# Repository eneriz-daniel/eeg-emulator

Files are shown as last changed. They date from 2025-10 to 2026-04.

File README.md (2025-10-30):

# EEG Emulation and Acquisition

> Documentation is available at: [https://eneriz-daniel.com/eeg-emulator/](https://eneriz-daniel.com/eeg-emulator/)

This repository contains the design files, code, and documentation for an EEG
emulation and acquisition system. The system is designed to emulate an EEG headset
using a custom PCB that demultiplexes signals from a National Instruments
USB-6212 Data Acquisition (DAQ) device, and to acquire EEG signals using an ADS1299
Analog-to-Digital Converter (ADC) connected to an Arduino Nano 33 BLE Sense.

## Repository Structure

The repository is organized into the following main directories and files:

- `docs/`: Documentation files for the project
    - `ads1299_driver/`: Python API reference for the ADS1299 driver
    - `assets/`: Images and diagrams used in documentation
    - `datasheets/`: Component datasheets and manuals
  
- `eeg_acquisition/`: EEG signal acquisition system components
    - `ADS1299driver.py`: Python wrapper for the ADS1299 driver
    - `design_files/`: KiCAD PCB and schematic files for the acquisition board
    - `micro/`: Arduino firmware for the ADS1299 driver
        - `src/`: C++ source code for the driver implementation

- `eeg_emulation/`: EEG signal emulation system components
    - `daq.py`: Python script for controlling the NI USB-6212 DAQ
    - `design_files/`: KiCAD PCB and schematic files for the demultiplexer board

- `test.py`: Example script demonstrating the integration between the EEG emulation and acquisition systems, including configuration of the ADS1299, signal generation, data acquisition, and visualization

## Requirements

### Software

- [Python](https://www.python.org/) 3.13 or later (for running the code and documentation)
    - Package manager, [`uv`](https://docs.astral.sh/uv/)
- [KiCAD](https://www.kicad.org/) 9 or later (for PCB design files)
- [PlatformIO](https://platformio.org/) (for Arduino development)

### Commercial hardware

- National Instruments NI USB-6212 Data Acquisition device

## Installation

- Clone the repository:

    ```bash
    git clone https://github.com/eneriz-daniel/eeg-emulator.git
    ```

- Install the required packages:

    ```bash
    uv sync --all-groups
    ```

## Software commands

- To serve the documentation locally:

    ```bash
    uv run mkdocs serve
    ```

- To check linting and formatting:

    ```bash
    uv run ruff check
    ```

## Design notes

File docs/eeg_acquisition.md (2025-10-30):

## The ADC

We have selected the [ADS1299](datasheets/ads1299.pdf) as the Anaglog-to-Digital
Converter (ADC) for our EEG acquisition system. The ADS1299 is a low-power,
24-bit, 8-channel ADC designed specifically for biopotential measurements,
making it an ideal choice for EEG applications. It features a high input impedance,
low noise, and a built-in programmable gain amplifier (PGA), which allows for
accurate signal acquisition from the scalp electrodes.

The ADS1299 can be connected to a microcontroller using the SPI interface,
which allows for fast data transfer and control of the ADC settings. We have created
an schematic design on a Kicad project to document how we have connected the
ADS1299 to an Arduino Nano 33 BLE Sense. The schematic includes the necessary
connections for power supply, ground, and the SPI interface. These schematic files
are available at `eeg_acquisition/design_files`.

## The driver

We have extended an existing driver for the ADS1299 to provide an interface through
serial communication. The driver is written in C++ and it includes functions for
initializing the ADC, configuring the settings, and reading the data from the ADC.
This driver has been tested with the Arduino Nano 33 BLE Sense and it is compatible with
the Arduino IDE and PlatformIO. The driver is available at `eeg_acquisition/micro`, and it is
composed of two main files:

- `ADS1299.cpp` contains the low-level implementation of the driver, including the
SPI commands to configure the ADC and read the data. The driver uses the Arduino SPI library
to communicate with the ADS1299.

- `ADS1299Manager.cpp` contains the high-level implementation of the driver, including
the functions to initialize the ADC, configure the settings, and read the data.
It also provides the functionality to interface with serial communication, allowing
for easy integration with other systems.

Additionally, we have created a Python wrapper for the driver, available at
`eeg_acquisition/ADS1299driver.py`. This wrapper is able to communicate with the
Arduino board through serial communication, allowing for easy integration with
Python applications. The wrapper includes functions for configuring the ADC,
reading the data and even live plotting the acquired signals, as shown below.
A complete reference for the wrapper is available [here](ads1299_driver/python.md).

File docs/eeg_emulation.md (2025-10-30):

EEG Demultiplexer PCB

## Introduction

We have designed a PCB to emulate an EEG headset by demultiplexing the
signals from a multiplexed EEG signal provided by a Data Acquisition (DAQ) device,
a [National Instruments USB-6212](datasheets/usb-621x-manual.pdf).

## Description of the PCB

The design files and schematics of the PCB are available in the `eeg_demultiplexer/design_files`
directory.

### Analog part

The PCB is designed to demultiplex the 8 channels of the EEG signal from the DAQ
device, thus it has an analog input `EEG` and 8 main outputs `AOUT0` to `AOUT7`.

The analog input `EEG` must be in the range of 0-5V, since it is demultiplexed
with a [74HC4051](datasheets/74HC_HCT4051.pdf) analog demultiplexer. The outputs
of the demultiplexer are connected to the connections `A0` to `A7`,
which can be useful for debugging purposes.

Then, the signal is passed through the following sample-and-hold circuit, which is
followed by a voltage divider.

EEG Demultiplexer Analog Part

The sample-and-hold circuit is built with diode, a 1nF capacitor and a
[TL082](datasheets/tl082.pdf) operational amplifier. The diode and the capacitor
are used to sample the signal coming from the demultiplexer. A switch is used to
to short the capacitor to ground to discharge it before sampling the next
signal. The switch is controlled by the `DCHG` signal.

The operational amplifier is configured with a non-inverting gain of 2 by using
resistors with the same value of 2.1kΩ. Additionally, setting the
reference of the feedback at +5V allows to offset the output voltage by -5V.

The output of the operational amplifier is externalized to the `AAMP0` to `AAMP7`
connections, which can be useful for debugging purposes.

Finally, the output of the operational amplifier is passed through a voltage divider
to reduce the voltage in a factor of 5000, using a resistors of 2MΩ and 400Ω.

### Digital part

To control the selected channel of the demultiplexer, the PCB has a [74HC191](datasheets/74HC191.pdf)
counter. The counter is configured to count up. It has 4 parallel inputs which are loaded
when the `CP` signal is low. The default value to be loaded in the counter is 7.
This counter is clocked with the `CLK` signal. The three least significant
outputs of the counter are used as the channel selection signals, they are connected
to the demultiplexer channel selection, and can be consulted at the `CHAN0` to `CHAN2`
connections.

Two 2-input AND gates are used to know when the counter has reached the value 7. This
gates are available in the [74HC08D](datasheets/74HC_HCT08.pdf) package.
The output of the AND gates is connected to one of the pins of jumper `J13`. Other
pin of the jumper `J13` is connected to the total count signal of the counter, which
is 1 when the counter has reached the value 15. The default position of the jumper
`J13` is to connect its central pin to the output of the AND gates, which identifies when the
counter has reached the value 7.

The central pin of the jumper `J13` is connected to the control of two switches [ADG719](datasheets/ADG719.pdf).
The input of the first switch is connected to the `CLK` signal, and the output
is connected to the `START` signal, which can be used to trigger the conversion
of an ADC sampling the demultiplexed signals. The input of the second switch is
connected to the negated `CLK` signal, which is generated with an inverter [74HC04](datasheets/74HC_HCT1G04.pdf).
The output of this second switch is connected to the `DISCHARGE` signal, which
is used to discharge the capacitor of the sample-and-hold circuit.

Therefore, the following diagram shows the behavior of the digital part of the PCB:

```kroki-wavedrom
{ signal:
    [
      { name: 'CLK',      wave: 'P........', period: 2},
      { name: 'CHAN',     wave: '=========', data: ['0', '1', '2', '3', '4', '5', '6', '7', '0'], period: 2},
      { name: 'J16',      wave: '0......10', period: 2},
      { name: 'START',    wave: '0.............10..'},
      { name: '~CLK',     wave: 'N........', period: 2},
      { name: 'DISCARGE', wave: '0..............10.'},
    ]
}
```

## PCB characterization

To ensure the PCB is working properly, we have coded a simple test program,
`eeg_emulation/daq.py`, that uses the [nidaqmx](https://pypi.org/project/nidaqmx/)
library to control a National Instruments USB-6212 DAQ device. This program configures
the DAQ to:

- Ensure the channel in the counter of the PCB is set to 7.
- Create a clock signal `CTR0`, whose output is at `PFI12` pin of the DAQ.
- Create an analog output signal with the multiplexed EEG signal at pin `AO0`
  using the signal at `PFI0` as clock signal.
- Set 8 analog input pins to read the demultiplexed signals before the voltage
  divider. The pins of the PCB are `AAMP0` to `AAMP7`, and the pins of the DAQ
  are `AI0` to `AI7`. This conversion is triggered by the `START` signal, which
  is connected to the  `PFI2` pin of the DAQ device.

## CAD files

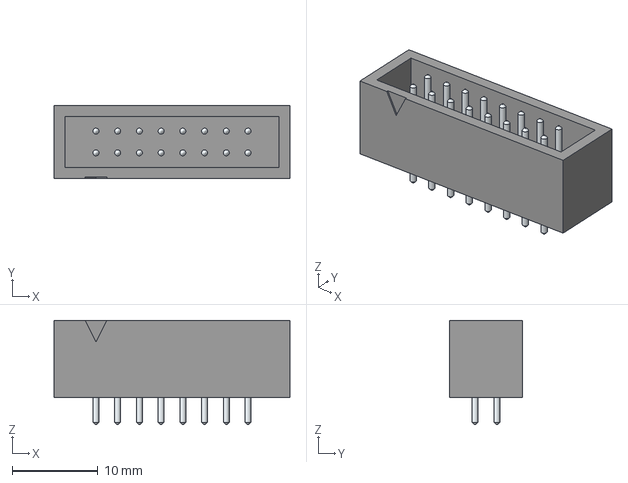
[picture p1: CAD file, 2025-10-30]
eeg_acquisition/design_files/3d-files/XG4C-1631.step
27.6 x 8.50 x 12.2 mm
LeadsArray

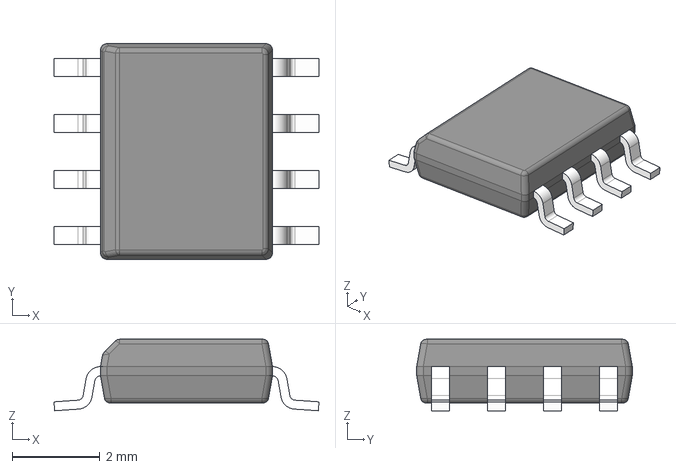
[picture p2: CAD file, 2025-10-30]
eeg_emulation/design_files/3d-models/LM2663MX_NOPB.stp
6.02 x 4.90 x 1.63 mm
BODY-SO
LEAD-D0008A x 8

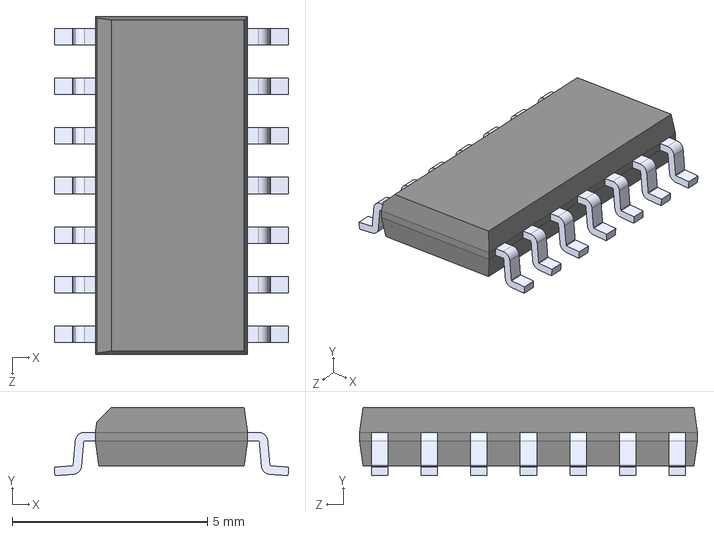
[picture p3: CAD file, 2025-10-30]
eeg_emulation/design_files/3d-models/74HC08D_653.step
6.00 x 1.75 x 8.65 mm

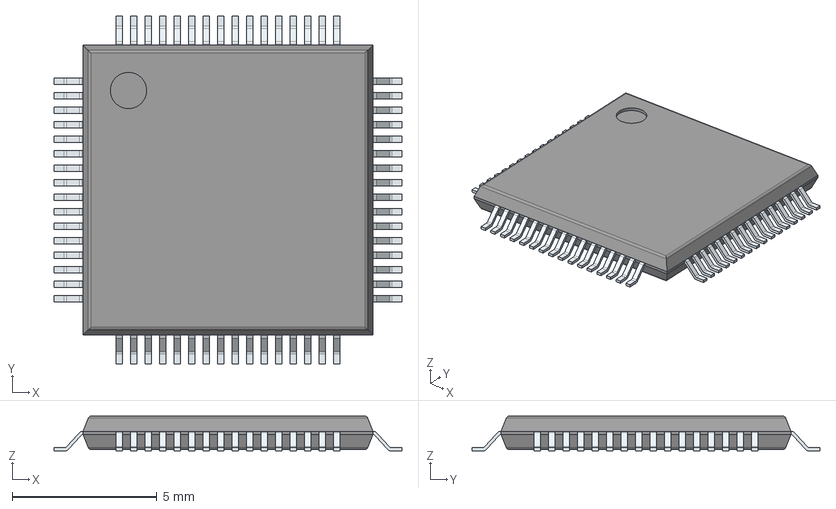
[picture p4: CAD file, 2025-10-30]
eeg_acquisition/design_files/3d-files/ADS1299-6PAG.step
12.0 x 12.0 x 1.20 mm
PinsArrayLR
PinsArrayTB

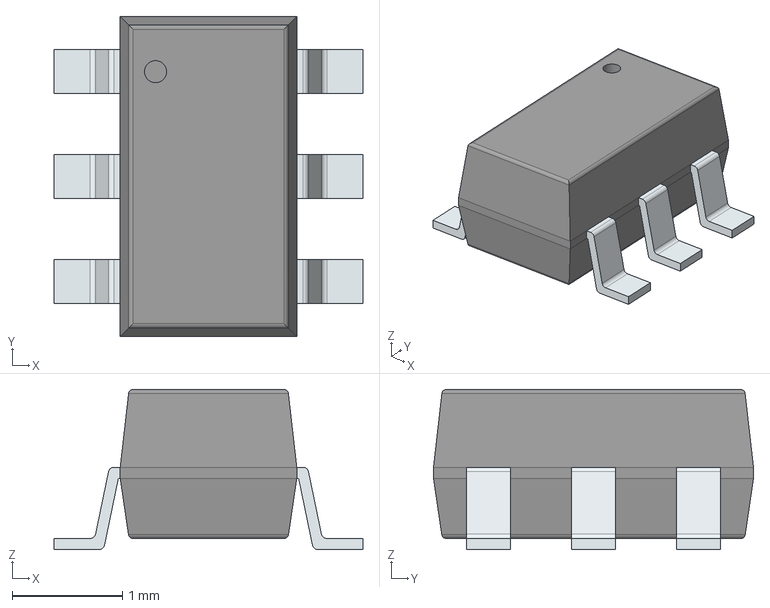
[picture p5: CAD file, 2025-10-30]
eeg_emulation/design_files/3d-models/ADG719BRTZ-REEL.step
2.80 x 2.90 x 1.45 mm
PinsArrayLR

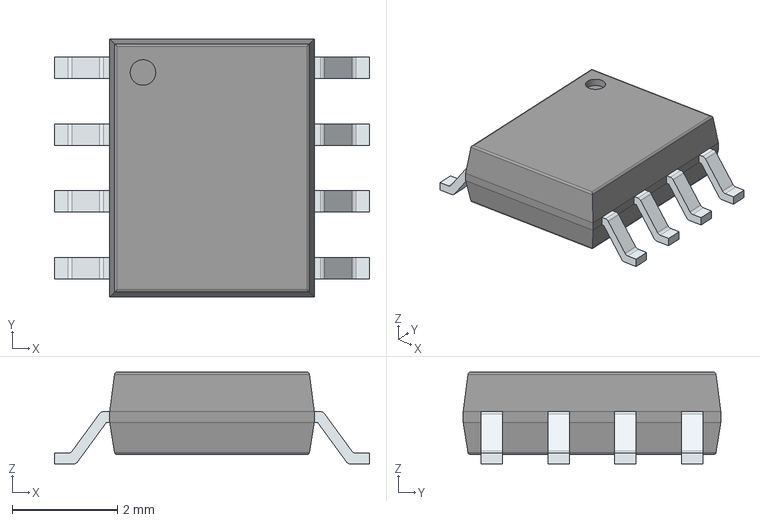
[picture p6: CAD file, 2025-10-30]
eeg_emulation/design_files/3d-models/TL082ID.step
6.00 x 4.91 x 1.75 mm
PinsArrayLR

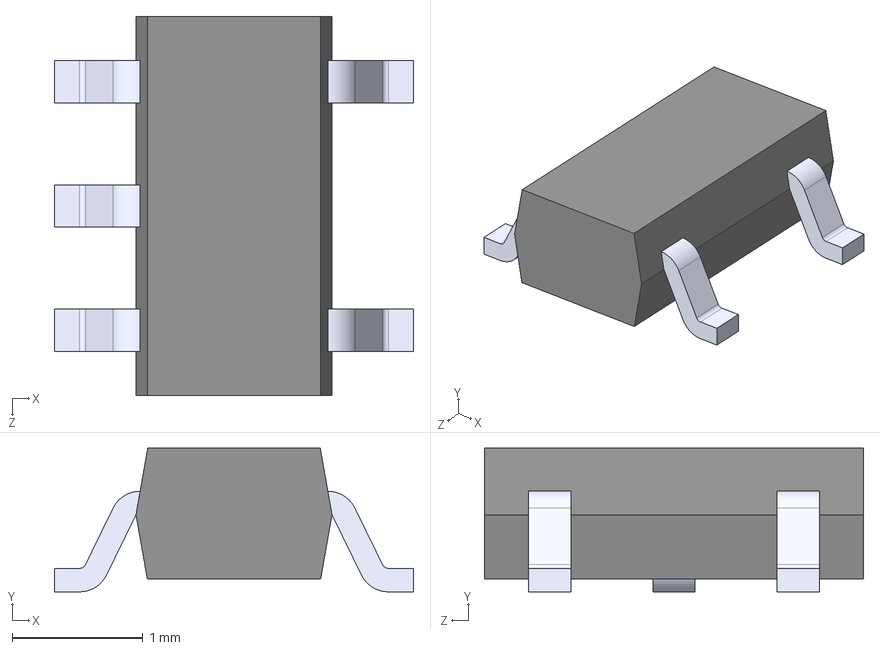
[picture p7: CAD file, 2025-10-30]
eeg_emulation/design_files/3d-models/74HC1G04GV,125.STEP
2.75 x 1.10 x 2.90 mm

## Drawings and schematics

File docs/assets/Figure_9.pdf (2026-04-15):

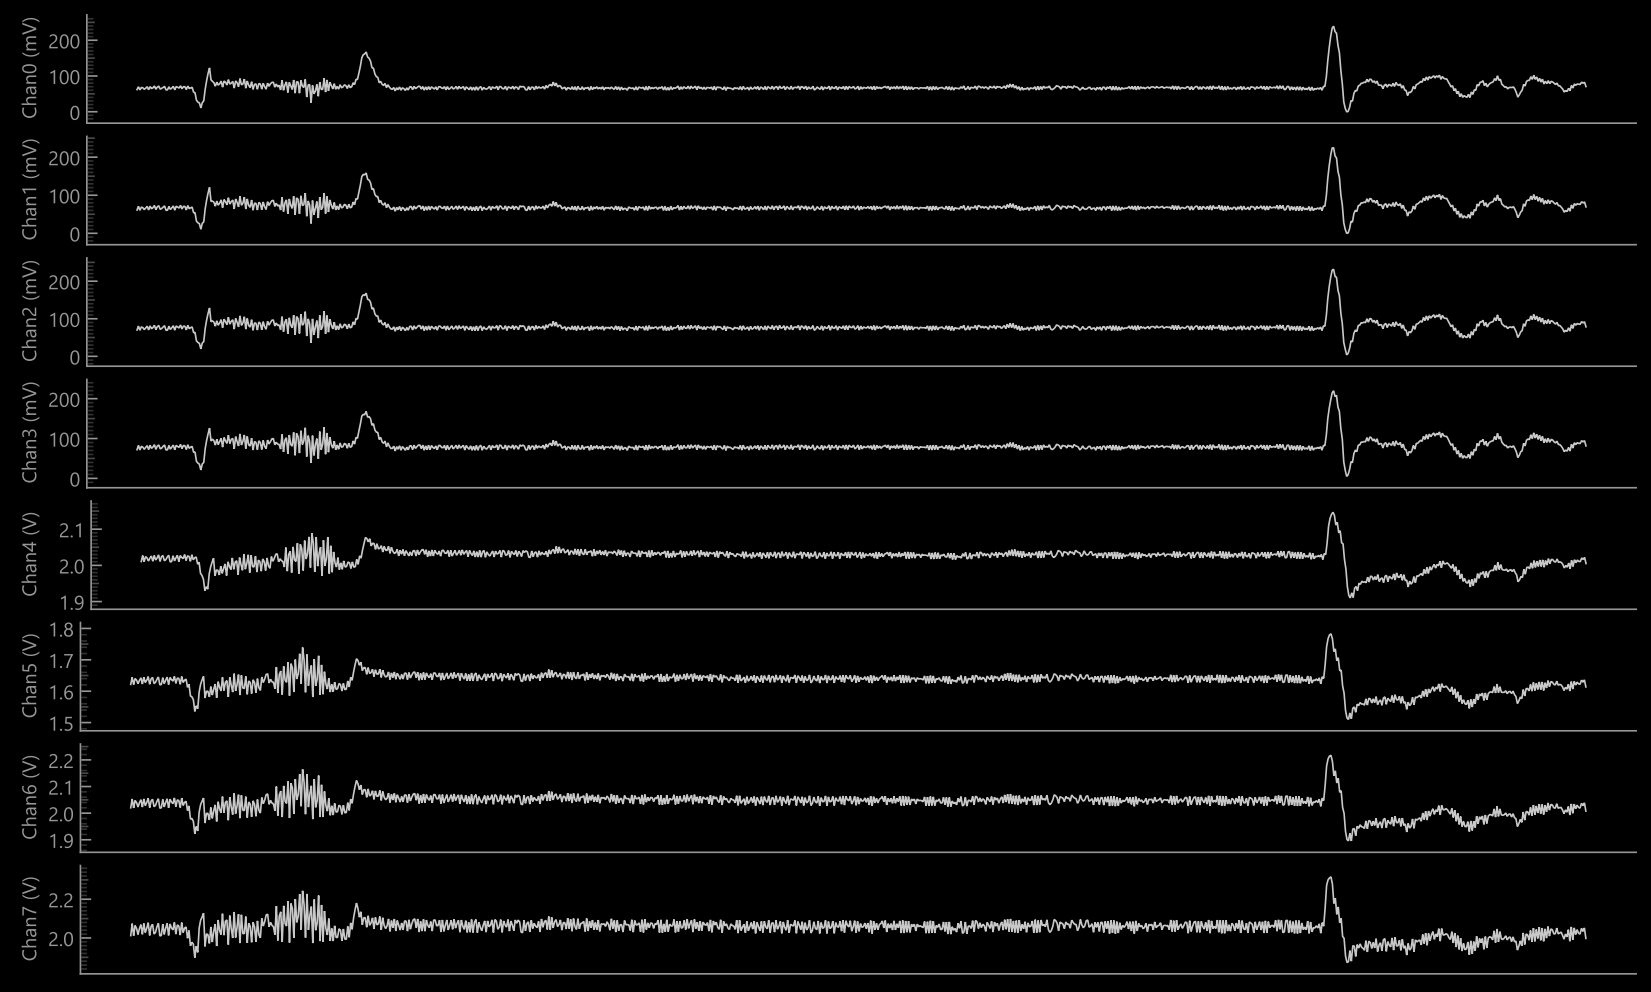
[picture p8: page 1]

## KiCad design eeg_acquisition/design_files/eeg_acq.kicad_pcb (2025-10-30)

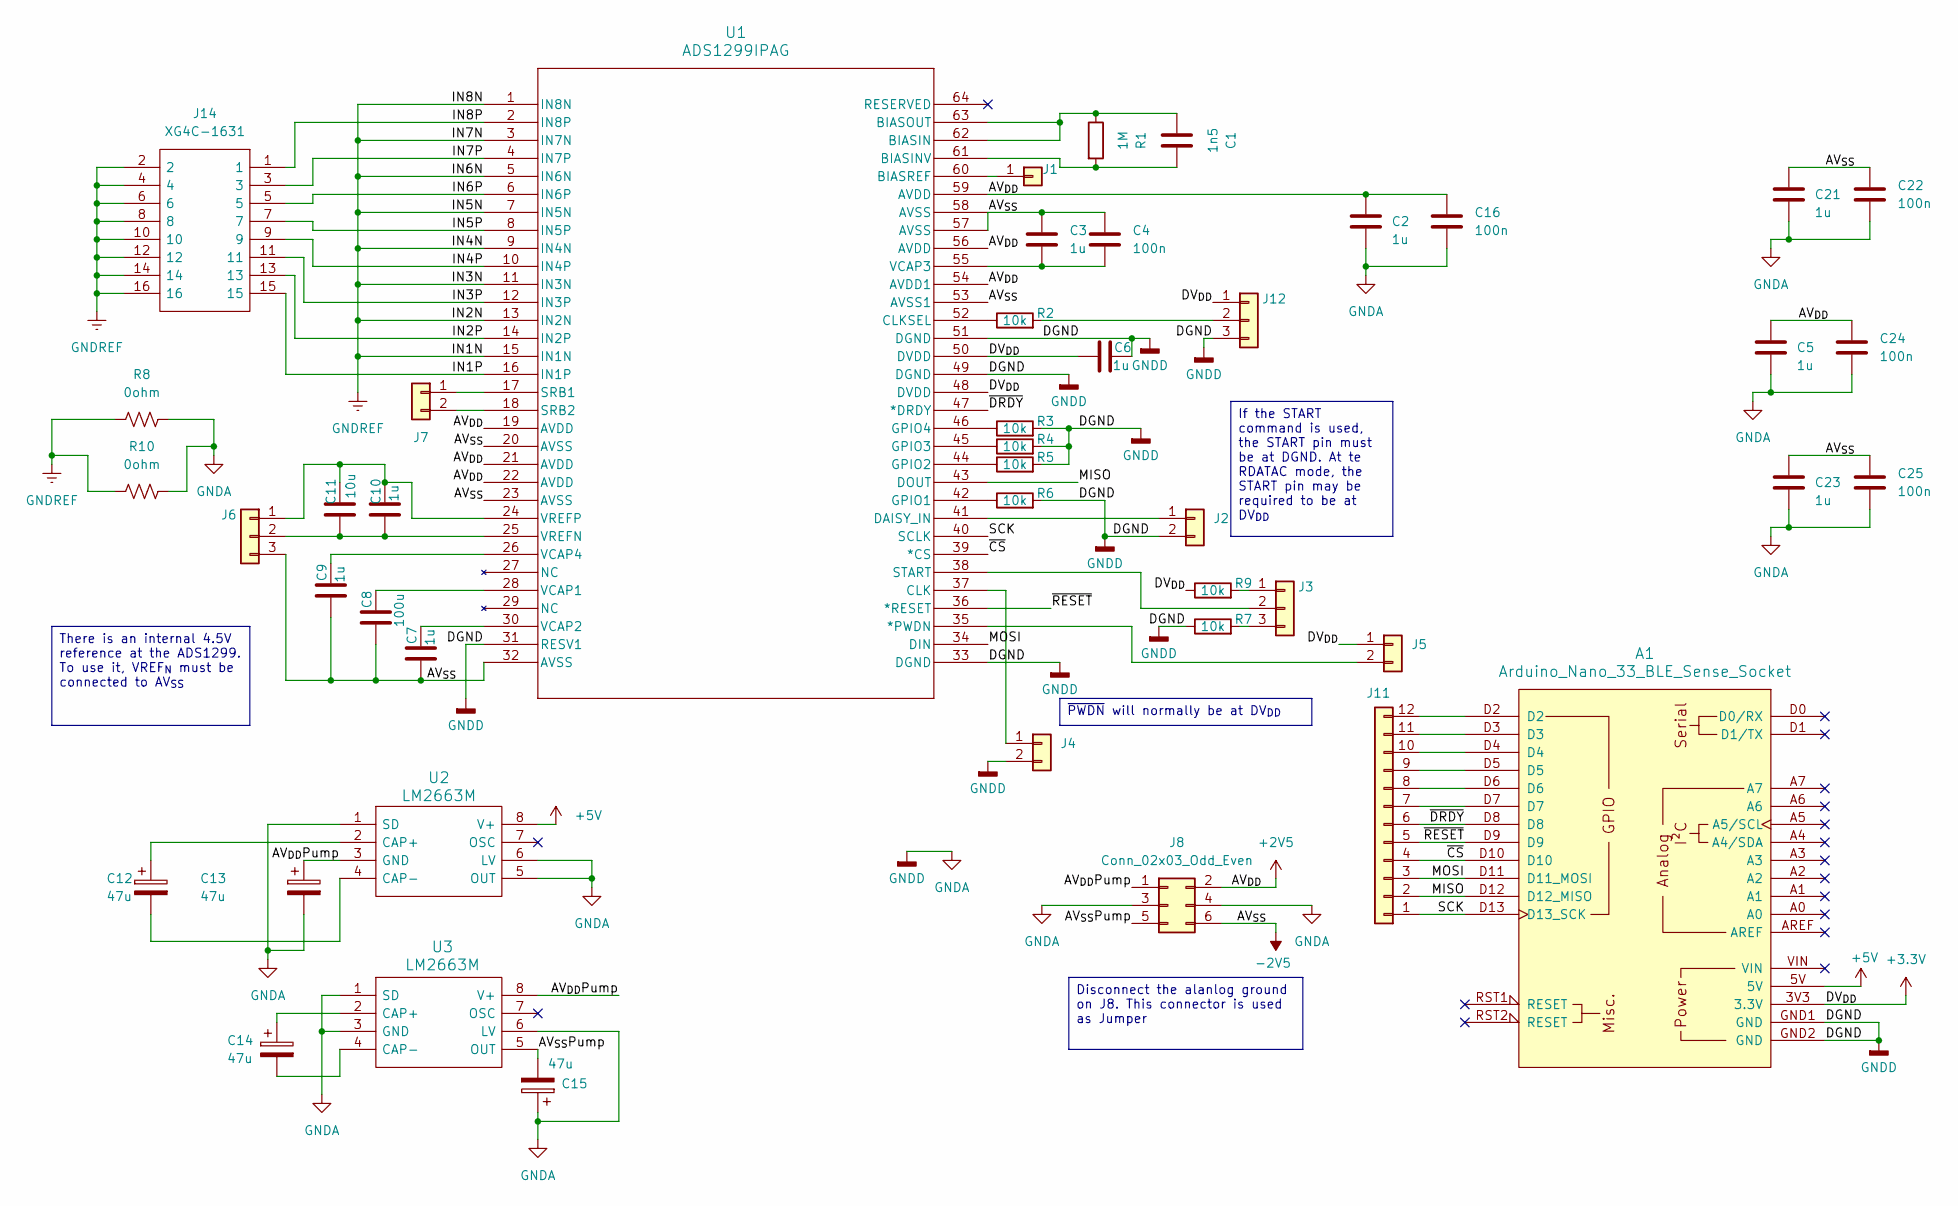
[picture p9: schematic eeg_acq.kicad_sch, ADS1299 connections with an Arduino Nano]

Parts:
A1: Arduino_Nano_33_BLE_Sense_Socket; Arduino_Nano_Every_Socket
C1: 1n5; C_0603_1608Metric_Pad1.08x0.95mm_HandSolder
C2, C3, C5, C6, C7, C9, C10, C21, C23: 1u; C_0603_1608Metric_Pad1.08x0.95mm_HandSolder
C4, C16, C22, C24, C25: 100n; C_0603_1608Metric_Pad1.08x0.95mm_HandSolder
C8: 100u; C_1206_3216Metric_Pad1.33x1.80mm_HandSolder
C11: 10u; C_0603_1608Metric_Pad1.08x0.95mm_HandSolder
C12, C13, C14, C15: 47u; CP_Radial_D10.0mm_P5.00mm
J1: BIASREF; PinSocket_1x01_P2.54mm_Vertical
J2, J4: DAISY_IN; PinSocket_1x02_P2.54mm_Vertical
J3: START; PinSocket_1x03_P2.54mm_Vertical
J5: ~PWDN; PinSocket_1x02_P2.54mm_Vertical
J6: VREF; PinSocket_1x03_P2.54mm_Vertical
J7: SRB; PinSocket_1x02_P2.54mm_Vertical
J8: Conn_02x03_Odd_Even; PinHeader_2x03_P2.54mm_Vertical
J11: PinHeader_1x12_P2.54mm_Vertical
J12: CLKSEL; PinSocket_1x03_P2.54mm_Vertical
J14: XG4C-1631; SHDR16W70P254_2X8_2760X850X900P; Manufacturer_Part_Number XG4C-1631; Mouser Part Number 653-XG4C-1631
R1: 1M; R_0603_1608Metric_Pad0.98x0.95mm_HandSolder
R2, R3, R4, R5, R6, R7, R9: 10k; R_0603_1608Metric_Pad0.98x0.95mm_HandSolder
R8, R10: 0ohm; R_0603_1608Metric
U1: ADS1299IPAG; PAG64_TEX
U2, U3: LM2663M; SOIC127P600X175-8N; Manufacturer_Part_Number LM2663M; Mouser Part Number 926-LM2663M

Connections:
+2V5: C2.1, C5.1, C16.1, C24.1, J8.2, U1.19 (AVDD), U1.21 (AVDD), U1.22 (AVDD), U1.54 (AVDD1), U1.56 (AVDD), U1.59 (AVDD)
+3.3V: A1.3V3 (3.3V), C6.2, J5.1, J12.1, R9.1, U1.48 (DVDD), U1.50 (DVDD)
+5V: A1.5V, U2.8 (V+)
-2V5: C3.1, C4.1, C7.2, C8.2, C9.2, C21.1, C22.1, C23.1, C25.1, J6.3, J8.6, U1.20 (AVSS), U1.23 (AVSS), U1.32 (AVSS), U1.53 (AVSS1), U1.57 (AVSS), U1.58 (AVSS)
/AV_{DD}Pump: C13.1, J8.1, U2.3 (GND), U3.8 (V+)
/AV_{SS}Pump: C15.2, J8.5, U3.5 (OUT)
/IN1P: J14.15, U1.16 (IN1P)
/IN2P: J14.13, U1.14 (IN2P)
/IN3P: J14.11, U1.12 (IN3P)
/IN4P: J14.9, U1.10 (IN4P)
/IN5P: J14.7, U1.8 (IN5P)
/IN6P: J14.5, U1.6 (IN6P)
/IN7P: J14.3, U1.4 (IN7P)
/IN8P: J14.1, U1.2 (IN8P)
/MISO: A1.D12 (D12_MISO), J11.2, U1.43 (DOUT)
/MOSI: A1.D11 (D11_MOSI), J11.3, U1.34 (DIN)
/SCK: A1.D13 (D13_SCK), J11.1, U1.40 (SCLK)
/~CS: A1.D10, J11.4, U1.39 (*CS)
/~DRDY: A1.D8, J11.6, U1.47 (*DRDY)
/~RESET: A1.D9, J11.5, U1.36 (*RESET)
GNDA: A1.GND1 (GND), A1.GND2 (GND), C2.2, C5.2, C6.1, C13.2, C15.1, C16.2, C21.2, C22.2, C23.2, C24.2, C25.2, J2.2, J4.2, J8.3, J8.4, J12.3, R3.2, R4.2, R5.2, R6.2, R7.1, R8.2, R10.2, U1.31 (RESV1), U1.33 (DGND), U1.49 (DGND), U1.51 (DGND), U2.1 (SD), U2.5 (OUT), U2.6 (LV), U3.1 (SD), U3.3 (GND), U3.6 (LV)
GNDREF: J14.2, J14.4, J14.6, J14.8, J14.10, J14.12, J14.14, J14.16, R8.1, R10.1, U1.1 (IN8N), U1.3 (IN7N), U1.5 (IN6N), U1.7 (IN5N), U1.9 (IN4N), U1.11 (IN3N), U1.13 (IN2N), U1.15 (IN1N)
unnamed: J1.1, U1.60 (BIASREF)
unnamed: J2.1, U1.41 (DAISY_IN)
unnamed: J3.1, R9.2
unnamed: J3.2, U1.38 (START)
unnamed: J3.3, R7.2
unnamed: J4.1, U1.37 (CLK)
unnamed: J5.2, U1.35 (*PWDN)
unnamed: C10.1, C11.1, J6.1, U1.24 (VREFP)
unnamed: C10.2, C11.2, J6.2, U1.25 (VREFN)
unnamed: J7.1, U1.17 (SRB1)
unnamed: J7.2, U1.18 (SRB2)
unnamed: A1.D7, J11.7
unnamed: A1.D6, J11.8
unnamed: A1.D5, J11.9
unnamed: A1.D4, J11.10
unnamed: A1.D3, J11.11
unnamed: A1.D2, J11.12
unnamed: J12.2, R2.2
unnamed: C1.1, R1.1, U1.62 (BIASIN), U1.63 (BIASOUT)
unnamed: C1.2, R1.2, U1.61 (BIASINV)
unnamed: R2.1, U1.52 (CLKSEL)
unnamed: R6.1, U1.42 (GPIO1)
unnamed: R5.1, U1.44 (GPIO2)
unnamed: R4.1, U1.45 (GPIO3)
unnamed: R3.1, U1.46 (GPIO4)
unnamed: C8.1, U1.28 (VCAP1)
unnamed: C7.1, U1.30 (VCAP2)
unnamed: C3.2, C4.2, U1.55 (VCAP3)
unnamed: C9.1, U1.26 (VCAP4)
unnamed: C12.1, U2.2 (CAP+)
unnamed: C12.2, U2.4 (CAP-)
unnamed: C14.1, U3.2 (CAP+)
unnamed: C14.2, U3.4 (CAP-)

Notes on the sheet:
~{PWDN} will normally be at DV_{DD}
Disconnect the alanlog ground on J8. This connector is used as Jumper
If the START command is used, the START pin must be at DGND. At te RDATAC mode, the START pin may be required to be at DV_{DD}
There is an internal 4.5V reference at the ADS1299. To use it, VREF_{N} must be connected to AV_{SS}

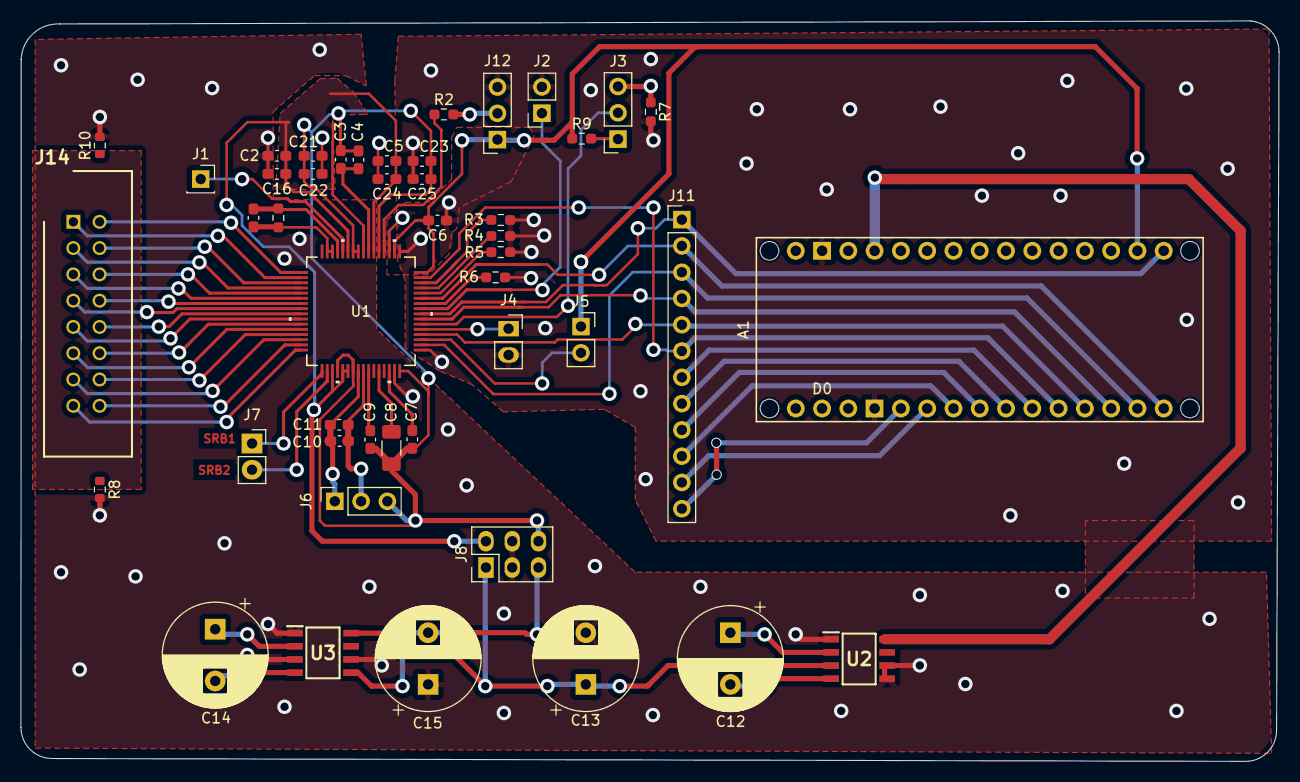
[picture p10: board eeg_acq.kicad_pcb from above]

Board: 2 copper layers, 121.6 x 71.6 mm, 46 parts (0 on the bottom side), 55 nets.

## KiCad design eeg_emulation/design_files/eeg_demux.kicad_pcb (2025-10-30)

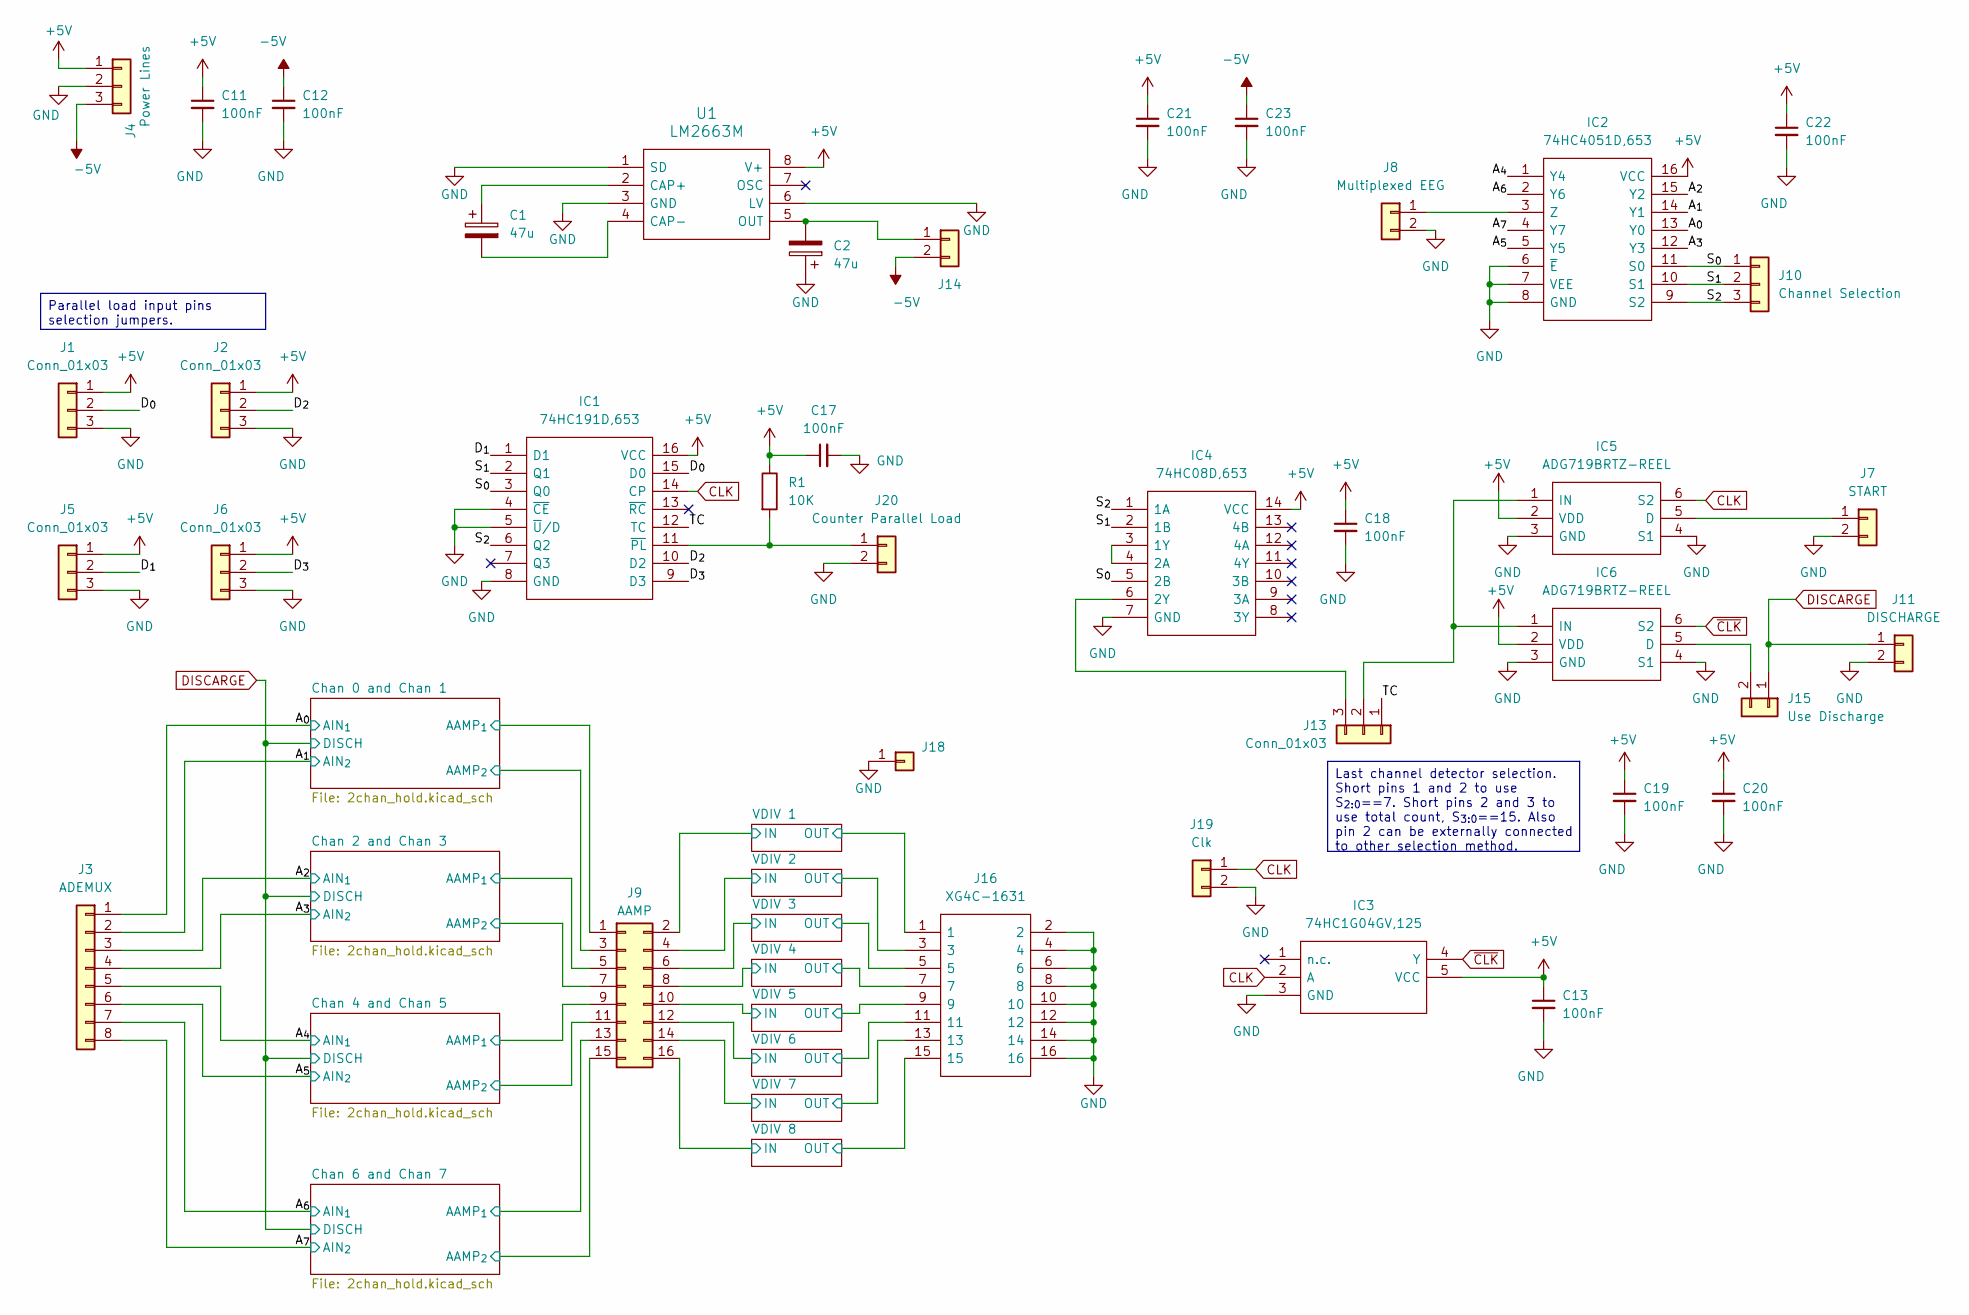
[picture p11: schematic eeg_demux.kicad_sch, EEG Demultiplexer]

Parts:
C1, C2: 47u; CP_Radial_D10.0mm_P5.00mm
C11, C12, C13, C17, C18, C19, C20, C21, C22, C23: 100nF; C_1206_3216Metric_Pad1.33x1.80mm_HandSolder
IC1: 74HC191D,653; SOIC127P600X175-16N; Mouser Part Number 771-HC191D653
IC2: 74HC4051D,653; 74HC4051D653; Mouser Part Number 771-74HC4051D-T
IC3: 74HC1G04GV,125; SOT95P275X110-5N; Mouser Part Number 771-74HC1G04GV
IC4: 74HC08D,653; SOIC127P600X175-14N; Mouser Part Number 771-74HC08D-T
IC5, IC6: ADG719BRTZ-REEL; SOT95P280X145-6N; Mouser Part Number 584-ADG719BRTZ-R
J1, J2, J5, J6, J13: Conn_01x03; PinHeader_1x03_P2.54mm_Vertical
J3: ADEMUX; PinHeader_1x08_P2.54mm_Vertical
J4: Power Lines; PinHeader_1x03_P2.54mm_Vertical
J7: START; PinHeader_1x02_P2.54mm_Vertical
J8: Multiplexed EEG; PinHeader_1x02_P2.54mm_Vertical
J9: AAMP; PinHeader_2x08_P2.54mm_Vertical
J10: Channel Selection; PinHeader_1x03_P2.54mm_Vertical
J11: DISCHARGE; PinHeader_1x02_P2.54mm_Vertical
J14: PinHeader_1x02_P2.54mm_Vertical
J15: Use Discharge; PinHeader_1x02_P2.54mm_Vertical
J16: XG4C-1631; SHDR16W70P254_2X8_2760X850X900P; Manufacturer_Part_Number XG4C-1631; Mouser Part Number 653-XG4C-1631
J18: PinHeader_1x01_P2.54mm_Vertical
J19: Clk; PinHeader_1x02_P2.54mm_Vertical
J20: Counter Parallel Load; PinHeader_1x02_P2.54mm_Vertical
R1: 10K; R_0603_1608Metric_Pad0.98x0.95mm_HandSolder
U1: LM2663M; SOIC127P600X175-8N; Manufacturer_Part_Number LM2663M; Mouser Part Number 926-LM2663M

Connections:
+5V: C11.1, C13.1, C17.1, C18.1, C19.1, C20.1, C21.1, C22.1, IC1.16 (VCC), IC2.16 (VCC), IC3.5 (VCC), IC4.14 (VCC), IC5.2 (VDD), IC6.2 (VDD), J1.1, J2.1, J4.1, J5.1, J6.1, R1.1, U1.8 (V+); also elsewhere on the board
-5V: C12.1, C23.1, J4.3, J14.2; also elsewhere on the board
/A_{0}: IC2.13 (Y0), J3.1; also elsewhere on the board
/A_{1}: IC2.14 (Y1), J3.2; also elsewhere on the board
/A_{2}: IC2.15 (Y2), J3.3; also elsewhere on the board
/A_{3}: IC2.12 (Y3), J3.4; also elsewhere on the board
/A_{4}: IC2.1 (Y4), J3.5; also elsewhere on the board
/A_{5}: IC2.5 (Y5), J3.6; also elsewhere on the board
/A_{6}: IC2.2 (Y6), J3.7; also elsewhere on the board
/A_{7}: IC2.4 (Y7), J3.8; also elsewhere on the board
/Chan 0 and Chan 1/AAMP_{1}: J9.1; also elsewhere on the board
/Chan 0 and Chan 1/AAMP_{2}: J9.3; also elsewhere on the board
/Chan 2 and Chan 3/AAMP_{1}: J9.5; also elsewhere on the board
/Chan 2 and Chan 3/AAMP_{2}: J9.7; also elsewhere on the board
/Chan 4 and Chan 5/AAMP_{1}: J9.9; also elsewhere on the board
/Chan 4 and Chan 5/AAMP_{2}: J9.11; also elsewhere on the board
/Chan 6 and Chan 7/AAMP_{1}: J9.13; also elsewhere on the board
/Chan 6 and Chan 7/AAMP_{2}: J9.15; also elsewhere on the board
/D_{0}: IC1.15 (D0), J1.2
/D_{1}: IC1.1 (D1), J5.2
/D_{2}: IC1.10 (D2), J2.2
/D_{3}: IC1.9 (D3), J6.2
/S_{0}: IC1.3 (Q0), IC2.11 (S0), IC4.5 (2B), J10.1
/S_{1}: IC1.2 (Q1), IC2.10 (S1), IC4.2 (1B), J10.2
/S_{2}: IC1.6 (Q2), IC2.9 (S2), IC4.1 (1A), J10.3
/TC: IC1.12 (TC), J13.1
/VDIV 1/IN: J9.2; also elsewhere on the board
/VDIV 1/OUT: J16.1; also elsewhere on the board
/VDIV 2/IN: J9.4; also elsewhere on the board
/VDIV 2/OUT: J16.3; also elsewhere on the board
/VDIV 3/IN: J9.6; also elsewhere on the board
/VDIV 3/OUT: J16.5; also elsewhere on the board
/VDIV 4/IN: J9.8; also elsewhere on the board
/VDIV 4/OUT: J16.7; also elsewhere on the board
/VDIV 5/IN: J9.10; also elsewhere on the board
/VDIV 5/OUT: J16.9; also elsewhere on the board
/VDIV 6/IN: J9.12; also elsewhere on the board
/VDIV 6/OUT: J16.11; also elsewhere on the board
/VDIV 7/IN: J9.14; also elsewhere on the board
/VDIV 7/OUT: J16.13; also elsewhere on the board
/VDIV 8/IN: J9.16; also elsewhere on the board
/VDIV 8/OUT: J16.15; also elsewhere on the board
CLK: IC1.14 (CP), IC3.2 (A), IC5.6 (S2), J19.1
DISCARGE: J11.1, J15.1; also elsewhere on the board
GND: C2.1, C11.2, C12.2, C13.2, C17.2, C18.2, C19.2, C20.2, C21.2, C22.2, C23.2, IC1.4 (~CE), IC1.5 (~U/D), IC1.8 (GND), IC2.6 (~E), IC2.7 (VEE), IC2.8 (GND), IC3.3 (GND), IC4.7 (GND), IC5.3 (GND), IC5.4 (S1), IC6.3 (GND), IC6.4 (S1), J1.3, J2.3, J4.2, J5.3, J6.3, J7.2, J8.2, J11.2, J16.2, J16.4, J16.6, J16.8, J16.10, J16.12, J16.14, J16.16, J18.1, J19.2, J20.2, U1.1 (SD), U1.3 (GND), U1.6 (LV); also elsewhere on the board
unnamed: IC1.11 (~PL), J20.1, R1.2
unnamed: IC2.3 (Z), J8.1
unnamed: IC4.3 (1Y), IC4.4 (2A)
unnamed: IC4.6 (2Y), J13.3
unnamed: IC5.5 (D), J7.1
unnamed: IC5.1 (IN), IC6.1 (IN), J13.2
unnamed: IC6.5 (D), J15.2
unnamed: C2.2, J14.1, U1.5 (OUT)
unnamed: C1.1, U1.2 (CAP+)
unnamed: C1.2, U1.4 (CAP-)
~CLK: IC3.4 (Y), IC6.6 (S2)

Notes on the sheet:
Last channel detector selection. Short pins 1 and 2 to use S_{2:0}==7. Short pins 2 and 3 to use total count, S_{3:0}==15. Also pin 2 can be externally connected to other selection method.
Parallel load input pins selection jumpers.

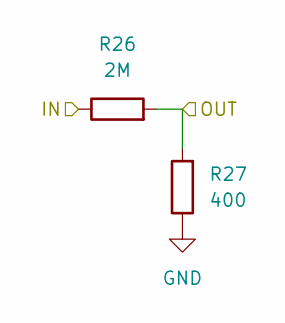
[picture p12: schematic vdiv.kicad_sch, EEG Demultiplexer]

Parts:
R26: 2M; R_0603_1608Metric_Pad0.98x0.95mm_HandSolder
R27: 400; R_0603_1608Metric_Pad0.98x0.95mm_HandSolder

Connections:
/VDIV 1/IN: R26.1; also elsewhere on the board
/VDIV 1/OUT: R26.2, R27.2; also elsewhere on the board
GND: R27.1; also elsewhere on the board

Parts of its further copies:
R28, R30, R32, R34, R36, R38, R40: 2M; R_0603_1608Metric_Pad0.98x0.95mm_HandSolder
R29, R31, R33, R35, R37, R39, R41: 400; R_0603_1608Metric_Pad0.98x0.95mm_HandSolder

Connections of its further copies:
/VDIV 2/IN: R28.1; also elsewhere on the board
/VDIV 2/OUT: R28.2, R29.2; also elsewhere on the board
/VDIV 3/IN: R30.1; also elsewhere on the board
/VDIV 3/OUT: R30.2, R31.2; also elsewhere on the board
/VDIV 4/IN: R32.1; also elsewhere on the board
/VDIV 4/OUT: R32.2, R33.2; also elsewhere on the board
/VDIV 5/IN: R34.1; also elsewhere on the board
/VDIV 5/OUT: R34.2, R35.2; also elsewhere on the board
/VDIV 6/IN: R36.1; also elsewhere on the board
/VDIV 6/OUT: R36.2, R37.2; also elsewhere on the board
/VDIV 7/IN: R38.1; also elsewhere on the board
/VDIV 7/OUT: R38.2, R39.2; also elsewhere on the board
/VDIV 8/IN: R40.1; also elsewhere on the board
/VDIV 8/OUT: R40.2, R41.2; also elsewhere on the board
GND: R29.1, R31.1, R33.1, R35.1, R37.1, R39.1, R41.1; also elsewhere on the board

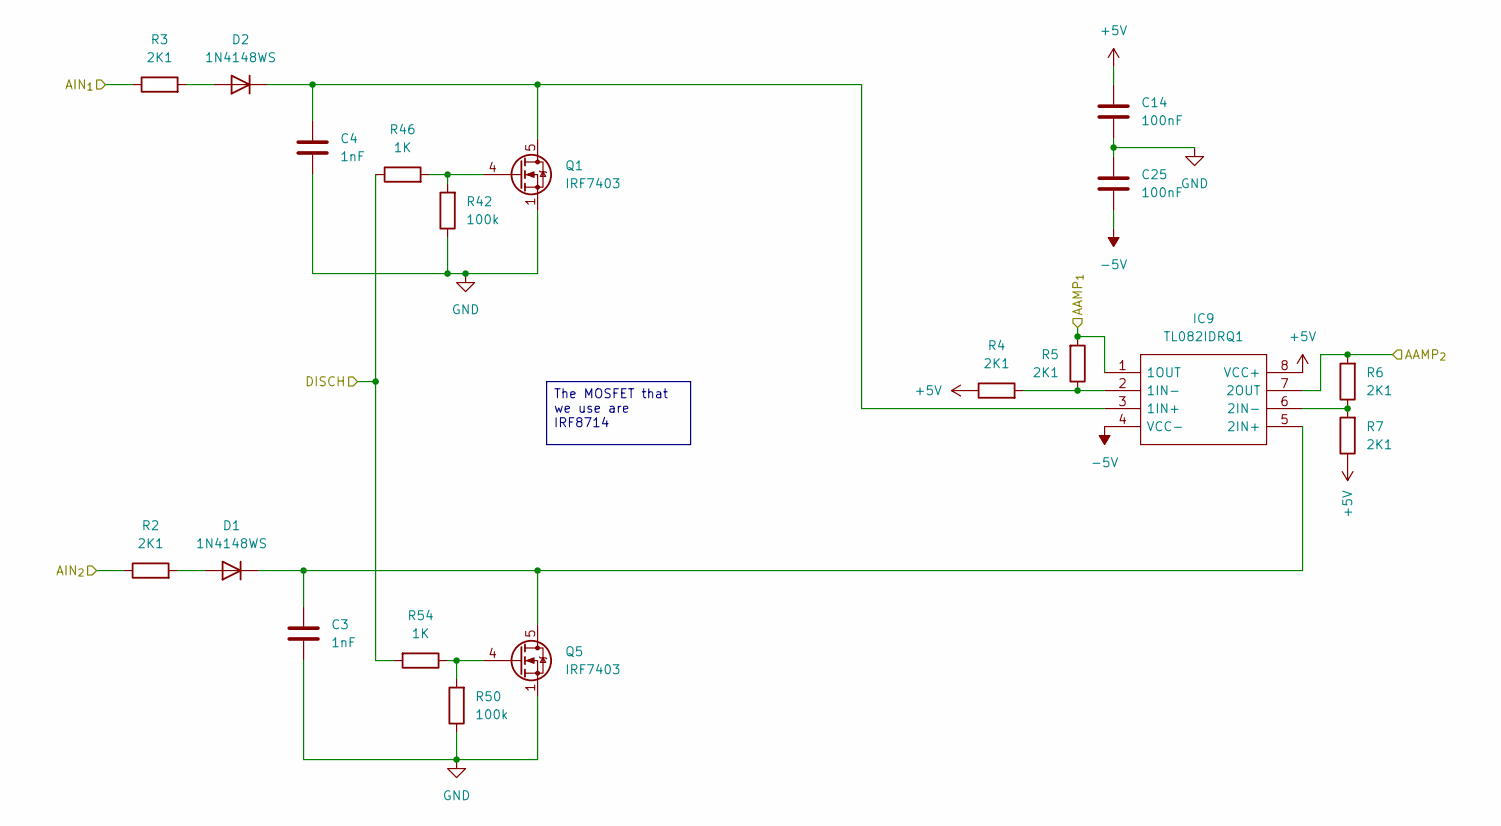
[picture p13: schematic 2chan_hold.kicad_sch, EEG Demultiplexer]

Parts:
C3, C4: 1nF; C_0603_1608Metric_Pad1.08x0.95mm_HandSolder
C14, C25: 100nF; C_0603_1608Metric_Pad1.08x0.95mm_HandSolder
D1, D2: 1N4148WS; D_1206_3216Metric_Pad1.42x1.75mm_HandSolder
IC9: TL082IDRQ1; SOIC127P600X175-8N; Mouser Part Number 595-TL082IDRQ1
Q1, Q5: IRF7403; SOIC-8_3.9x4.9mm_P1.27mm
R2, R3, R4, R5, R6, R7: 2K1; R_0603_1608Metric_Pad0.98x0.95mm_HandSolder
R42, R50: 100k; R_0603_1608Metric_Pad0.98x0.95mm_HandSolder
R46, R54: 1K; R_0603_1608Metric_Pad0.98x0.95mm_HandSolder

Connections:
+5V: C14.1, IC9.8 (VCC+), R4.1, R7.1; also elsewhere on the board
-5V: C25.2, IC9.4 (VCC-); also elsewhere on the board
/A_{0}: R3.1; also elsewhere on the board
/A_{1}: R2.1; also elsewhere on the board
/Chan 0 and Chan 1/AAMP_{1}: IC9.1 (1OUT), R5.2; also elsewhere on the board
/Chan 0 and Chan 1/AAMP_{2}: IC9.7 (2OUT), R6.2; also elsewhere on the board
DISCARGE: R46.1, R54.2; also elsewhere on the board
GND: C3.2, C4.2, C14.2, C25.1, Q1.1 (S), Q1.2 (S), Q1.3 (S), Q5.1 (S), Q5.2 (S), Q5.3 (S), R42.1, R50.1; also elsewhere on the board
unnamed: D1.2 (A), R2.2
unnamed: C3.1, D1.1 (K), IC9.5 (2IN+), Q5.5 (D), Q5.6 (D), Q5.7 (D), Q5.8 (D)
unnamed: D2.2 (A), R3.2
unnamed: C4.1, D2.1 (K), IC9.3 (1IN+), Q1.5 (D), Q1.6 (D), Q1.7 (D), Q1.8 (D)
unnamed: IC9.2 (1IN-), R4.2, R5.1
unnamed: IC9.6 (2IN-), R6.1, R7.2
unnamed: Q1.4 (G), R42.2, R46.2
unnamed: Q5.4 (G), R50.2, R54.1

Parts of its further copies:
C5, C6, C7, C8, C9, C10: 1nF; C_0603_1608Metric_Pad1.08x0.95mm_HandSolder
C15, C16, C24, C26, C27, C28: 100nF; C_0603_1608Metric_Pad1.08x0.95mm_HandSolder
D3, D4, D5, D6, D7, D8: 1N4148WS; D_1206_3216Metric_Pad1.42x1.75mm_HandSolder
IC12, IC15, IC18: TL082IDRQ1; SOIC127P600X175-8N; Mouser Part Number 595-TL082IDRQ1
Q2, Q3, Q4, Q6, Q7, Q8: IRF7403; SOIC-8_3.9x4.9mm_P1.27mm
R8, R9, R10, R11, R12, R13, R14, R15, R16, R17, R18, R19, R20, R21, R22, R23, R24, R25: 2K1; R_0603_1608Metric_Pad0.98x0.95mm_HandSolder
R43, R44, R45, R51, R52, R53: 100k; R_0603_1608Metric_Pad0.98x0.95mm_HandSolder
R47, R48, R49, R55, R56, R57: 1K; R_0603_1608Metric_Pad0.98x0.95mm_HandSolder

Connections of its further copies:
+5V: C15.1, C16.1, C24.1, IC12.8 (VCC+), IC15.8 (VCC+), IC18.8 (VCC+), R10.1, R13.1, R16.1, R19.1, R22.1, R25.1; also elsewhere on the board
-5V: C26.2, C27.2, C28.2, IC12.4 (VCC-), IC15.4 (VCC-), IC18.4 (VCC-); also elsewhere on the board
/A_{2}: R9.1; also elsewhere on the board
/A_{3}: R8.1; also elsewhere on the board
/A_{4}: R15.1; also elsewhere on the board
/A_{5}: R14.1; also elsewhere on the board
/A_{6}: R21.1; also elsewhere on the board
/A_{7}: R20.1; also elsewhere on the board
/Chan 2 and Chan 3/AAMP_{1}: IC12.1 (1OUT), R11.2; also elsewhere on the board
/Chan 2 and Chan 3/AAMP_{2}: IC12.7 (2OUT), R12.2; also elsewhere on the board
/Chan 4 and Chan 5/AAMP_{1}: IC15.1 (1OUT), R17.2; also elsewhere on the board
/Chan 4 and Chan 5/AAMP_{2}: IC15.7 (2OUT), R18.2; also elsewhere on the board
/Chan 6 and Chan 7/AAMP_{1}: IC18.1 (1OUT), R23.2; also elsewhere on the board
/Chan 6 and Chan 7/AAMP_{2}: IC18.7 (2OUT), R24.2; also elsewhere on the board
DISCARGE: R47.1, R48.1, R49.1, R55.2, R56.2, R57.2; also elsewhere on the board
GND: C5.2, C6.2, C7.2, C8.2, C9.2, C10.2, C15.2, C16.2, C24.2, C26.1, C27.1, C28.1, Q2.1 (S), Q2.2 (S), Q2.3 (S), Q3.1 (S), Q3.2 (S), Q3.3 (S), Q4.1 (S), Q4.2 (S), Q4.3 (S), Q6.1 (S), Q6.2 (S), Q6.3 (S), Q7.1 (S), Q7.2 (S), Q7.3 (S), Q8.1 (S), Q8.2 (S), Q8.3 (S), R43.1, R44.1, R45.1, R51.1, R52.1, R53.1; also elsewhere on the board
unnamed: D3.2 (A), R8.2
unnamed: C5.1, D3.1 (K), IC12.5 (2IN+), Q6.5 (D), Q6.6 (D), Q6.7 (D), Q6.8 (D)
unnamed: D4.2 (A), R9.2
unnamed: C6.1, D4.1 (K), IC12.3 (1IN+), Q2.5 (D), Q2.6 (D), Q2.7 (D), Q2.8 (D)
unnamed: D5.2 (A), R14.2
unnamed: C7.1, D5.1 (K), IC15.5 (2IN+), Q7.5 (D), Q7.6 (D), Q7.7 (D), Q7.8 (D)
unnamed: D6.2 (A), R15.2
unnamed: C8.1, D6.1 (K), IC15.3 (1IN+), Q3.5 (D), Q3.6 (D), Q3.7 (D), Q3.8 (D)
unnamed: D7.2 (A), R20.2
unnamed: C9.1, D7.1 (K), IC18.5 (2IN+), Q8.5 (D), Q8.6 (D), Q8.7 (D), Q8.8 (D)
unnamed: D8.2 (A), R21.2
unnamed: C10.1, D8.1 (K), IC18.3 (1IN+), Q4.5 (D), Q4.6 (D), Q4.7 (D), Q4.8 (D)
unnamed: IC12.2 (1IN-), R10.2, R11.1
unnamed: IC12.6 (2IN-), R12.1, R13.2
unnamed: IC15.2 (1IN-), R16.2, R17.1
unnamed: IC15.6 (2IN-), R18.1, R19.2
unnamed: IC18.2 (1IN-), R22.2, R23.1
unnamed: IC18.6 (2IN-), R24.1, R25.2
unnamed: Q2.4 (G), R43.2, R47.2
unnamed: Q3.4 (G), R44.2, R48.2
unnamed: Q4.4 (G), R45.2, R49.2
unnamed: Q6.4 (G), R51.2, R55.1
unnamed: Q7.4 (G), R52.2, R56.1
unnamed: Q8.4 (G), R53.2, R57.1

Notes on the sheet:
The MOSFET that we use are IRF8714

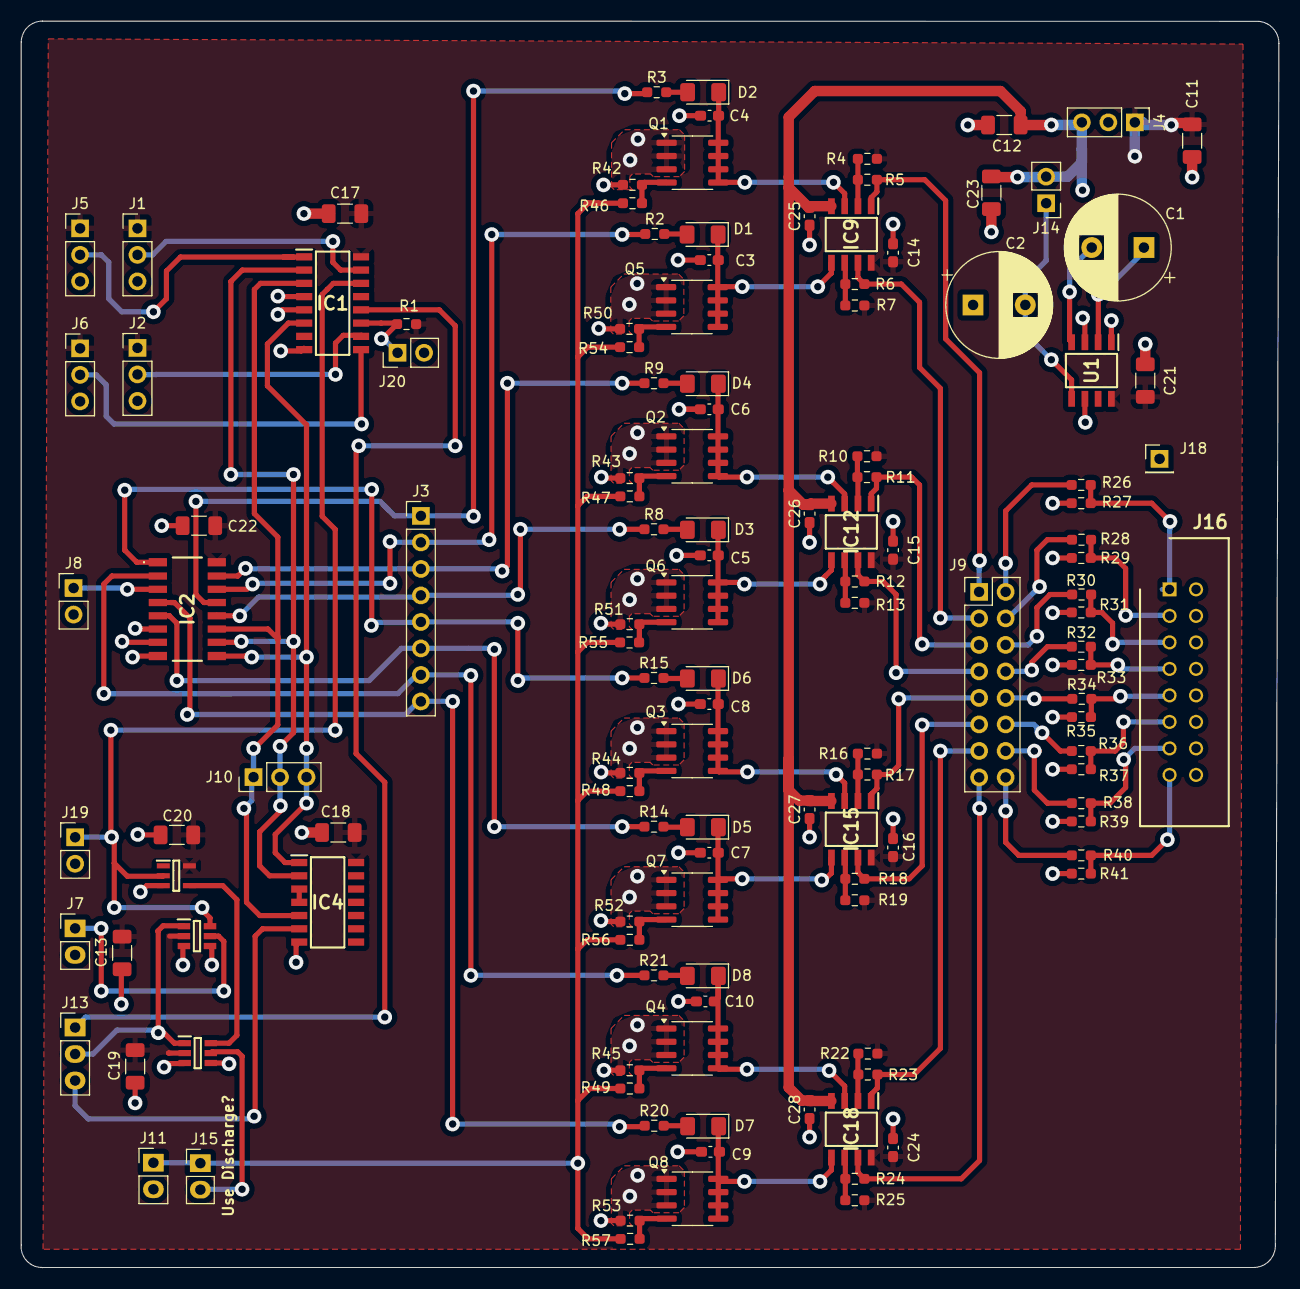
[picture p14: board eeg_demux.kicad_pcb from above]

Board: 2 copper layers, 120.5 x 119.4 mm, 130 parts (0 on the bottom side), 88 nets.

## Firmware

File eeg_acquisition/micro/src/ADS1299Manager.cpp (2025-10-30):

// The modifications made by Daniel Enériz are licensed under the GNU General Public License v3.0.
//
// Copyright (C) 2024 Daniel Enériz
// 
// This file is part of ADS1299 driver.
// 
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
//  ADS1299Manager.cpp
//  Part of the Arduino Library for the ADS1299 Shield
//  Created by Chip Audette, Fall 2013
//

#include <ADS1299Manager.h>

typedef long int32;
//typedef byte uint8_t;


/**
 * @brief Initializes the ADS1299Manager object.
 * 
 * This function initializes the ADS1299Manager object by calling the initialize
 * function of the ADS1299 class, setting the verbose flag to false, and resetting
 * the ADS1299 device. It also sets the number of channels for all boards based
 * on the isDaisy parameter.
 * 
 * @param isDaisy A bool value indicating whether the daisy chain is used.
 */
void ADS1299Manager::initialize(bool isDaisy) 
{
    ADS1299::initialize(PIN_DRDY,PIN_RST,PIN_CS,SCK_MHZ,isDaisy); // (DRDY pin, RST pin, CS pin, SCK frequency in MHz);
    delay(100);
        
    verbose = false; // Disable register-level verbosity
	outputMode = OUTPUT_TYPE_TEXT;  //default output mode is text
	isRunning = false;
	managerVerbose = true; // Enable manager-level verbosity
	batchSize = 0; // Initialize batch size to 0

	nChans = NCHAN_PER_BOARD;
    if (isDaisy) nChans = 2*NCHAN_PER_BOARD;

    reset();
};


/**
 * @brief Resets the ADS1299 device and turns off all channels.
 * 
 * This function sends a RESET command to the ADS1299 device to reset all its registers to default values.
 * It then exits the Read Data Continuous mode to allow communication with the ADS1299.
 * After a delay of 100 milliseconds, it turns off all channels by deactivating them.
 * 
 * @note This function assumes that the ADS1299 device is already initialized and connected.
 */
void ADS1299Manager::reset(void)
{
    ADS1299::RESET();             // send RESET command to default all registers
    ADS1299::SDATAC();            // exit Read Data Continuous mode to communicate
                                  // with ADS
	
	if (managerVerbose) {
		Serial.println("Resetting ADS1299");
	}
    
    delay(100);

	activateInternalReference(); // Activate the internal reference

	isRunning = false;

};


/**
 * @brief Activates the internal reference of the ADS1299Manager.
 * 
 * This function sets the CONFIG3 register of the ADS1299 device to enable the
 * internal reference. The internal reference is used as a voltage reference for
 * the ADC conversion.
 * 
 * @note This function assumes that the ADS1299 device is already initialized
 * and connected.
 */
void ADS1299Manager::activateInternalReference(void) {
    ADS1299::WREG(CONFIG3,0b11100000); delay(1);
	if (managerVerbose) {
		Serial.println("Activating internal reference");
	}
};


/**
 * @brief Deactivates the given channel of the ADS1299 device.
 * 
 * This function deactivates the given channel of the ADS1299 device by setting
 * the left-most bit of the corresponding CHnSET register to 1. This bit is used
 * to shut down the channel.
 * 
 * @param N The channel number to be deactivated.
 * 
 * @note This function assumes that the ADS1299 device is already initialized
 * and connected.
 * @note The channel number N is one-referenced (i.e., [1...N]), not [0...N-1].
 * @note The channel number N must be between 1 and 8. If the device is
 * daisy-chained, it will deactivate both the N-th channel of the master board
 * and the N-th channel of the slave board. Remember that in a daisy-chained
 * configuration, both boards share the same configuration.
 */
void ADS1299Manager::deactivateChannel(int N)
{
    byte reg, config;
        
    // Verify that the channel number is valid
    if ((N < 1) || (N > NCHAN_PER_BOARD)) return;
    
    // Disable any data collection
    ADS1299::SDATAC(); delay(1);

	isRunning = false;

    // Shut down the channel without modifying the other bits of the CHnSET register
    int N_zeroRef = constrain(N-1,0,NCHAN_PER_BOARD-1);
    reg = CH1SET+(byte)N_zeroRef;
    config = ADS1299::RREG(reg); delay(1);
    bitSet(config,7);  //left-most bit (bit 7) = 1, so this shuts down the channel
    ADS1299::WREG(reg,config); delay(1);
};


/**
 * @brief Deactivates all channels of the ADS1299 device.
 * 
 * This function deactivates all channels of the ADS1299 device by calling the
 * deactivateChannel function for each channel.
 * 
 * @note This function assumes that the ADS1299 device is already initialized
 * and connected.
 */
void ADS1299Manager::deactivateAllChannels(void) {
    for (int chan=1; chan <= NCHAN_PER_BOARD; chan++) {
        deactivateChannel(chan);
    }
};

/**
 * @brief Powers up the given channel of the ADS1299 device.
 * 
 * This function activates the given channel of the ADS1299 device by setting
 * the left-most bit of the corresponding CHnSET register to 0. This bit is used
 * to power up the channel.
 * 
 * @param N The channel number to be activated.
 * 
 * @note This function assumes that the ADS1299 device is already initialized
 * and connected.
 * @note The channel number N is one-referenced (i.e., [1...N]), not [0...N-1].
 * @note The channel number N must be between 1 and 8. If the device is
 * daisy-chained, it will deactivate both the N-th channel of the master board
 * and the N-th channel of the slave board. Remember that in a daisy-chained
 * configuration, both boards share the same configuration.
 */
void ADS1299Manager::enableChannel(int N)
{
    byte reg, config;
        
    // Check the inputs
    if ((N < 1) || (N > NCHAN_PER_BOARD)) return;
    
    // Disable any data collection
    ADS1299::SDATAC(); delay(1);

    // Read the previous configuration
    int N_zeroRef = constrain(N-1,0,NCHAN_PER_BOARD-1);
    reg = CH1SET+(byte)N_zeroRef;
    config = ADS1299::RREG(reg); delay(1);

    // Activate the channel
    bitClear(config,7);  //left-most bit (bit 7) = 0, so this activates the channel

    // Write the new configuration
    ADS1299::WREG(reg,config); delay(1);

	isRunning = false;
};

/**
 * @brief Activate all channels of the ADS1299 device.
 * 
 * This function activates all channels of the ADS1299 device by calling the
 * enableChannel function for each channel.
 * 
 * @note This function assumes that the ADS1299 device is already initialized
 */
void ADS1299Manager::enableAllChannels(void) {
    for (int chan=1; chan <= NCHAN_PER_BOARD; chan++) {
        enableChannel(chan);
    }
};

/**
 * @brief Sets the clock output of the ADS1299 device.
 * 
 * @param enable A bool value indicating whether the clock output should be
 * enabled (true) or disabled (false).
 */
void ADS1299Manager::setClockOutput(bool enable) {

	// Disable any data collection
	ADS1299::SDATAC(); delay(1);

	byte config = ADS1299::RREG(CONFIG1); delay(1);

	if (enable) bitSet(config,5);
	else bitClear(config,5);

	ADS1299::WREG(CONFIG1,config); delay(1);
};

/**
 * @brief Configures the data rate of the ADS1299 device.
 * 
 * This function configures the data rate of the ADS1299 device by setting the
 * data rate bits, [2:0], of the CONFIG1 register.
 * 
 * @param dataRateCode The data rate code to be set. Available data rate codes
 * have been defined as macros with the format ADS_DR_XXX, where XXX is the data
 * rate value in decimal samples per second.
 */
void ADS1299Manager::configureDataRate(byte dataRateCode) {

	// Disable any data collection
	ADS1299::SDATAC(); delay(1);

	byte config = ADS1299::RREG(CONFIG1); delay(1);
	dataRateCode &= 0b00000111; //only the last three bits should be used
	config = (config & 0b11111000) | dataRateCode; // Bitwise AND to clear the data rate bits and Bitwise OR to set the new data rate bits

	// Write the new configuration
	ADS1299::WREG(CONFIG1,config); delay(1);
};

/**
 * @brief Sets the gain of the given channel of the ADS1299 device.
 * 
 * This function sets the gain of the given channel of the ADS1299 device by
 * configuring the gain bits, [6:4], of the corresponding CHnSET register.
 * 
 * @param N The channel number to be configured.
 * @param gainCode The gain code to be set. Available gain codes have been
 * defined as macros with the format ADS_GAINXX, where XX is the gain value in
 * decimal.
 * 
 * @note This function assumes that the ADS1299 device is already initialized
 * and connected.
 * @note The channel number N is one-referenced (i.e., [1...N]), not [0...N-1].
 * @note The channel number N must be between 1 and 8. If the device is
 * daisy-chained, it will deactivate both the N-th channel of the master board
 * and the N-th channel of the slave board. Remember that in a daisy-chained
 * configuration, both boards share the same configuration.
 */
void ADS1299Manager::configureChannelGain(int N, byte gainCode)
{
    byte reg, config;
        
    // Check the inputs
    if ((N < 1) || (N > NCHAN_PER_BOARD)) return;
    
    // Disable any data collection
    ADS1299::SDATAC(); delay(1);

    // Read the previous configuration
    int N_zeroRef = constrain(N-1,0,NCHAN_PER_BOARD-1);
    reg = CH1SET+(byte)N_zeroRef;
    config = ADS1299::RREG(reg); delay(1);

    // Configure the gain
    gainCode = gainCode & 0b01110000;          // Bitwise AND to get just the bits we want and set the rest to zero
    config = (config & 0b10001111) | gainCode; // Bitwise AND to clear the gain bits and Bitwise OR to set the new gain bits

    // Write the new configuration
    ADS1299::WREG(reg,config); delay(1);

	isRunning = false;
};

/**
 * @brief Sets the input configuration of the given channel of the ADS1299 device.
 * 
 * This function sets the input configuration of the given channel of the ADS1299
 * device by configuring the input bits, [2:0], of the corresponding CHnSET,
 * register, which are also called the MUX bits.
 * 
 * @param N Channel number to be configured.
 * @param inputCode Input code to be set. Available input codes have been defined
 * as macros with the format ADSINPUT_XXXX, where XXXX is the input configuration,
 * that can be NORMAL, SHORTED, or TESTSIG.
 * 
 * @note This function assumes that the ADS1299 device is already initialized
 * and connected.
 * @note The channel number N is one-referenced (i.e., [1...N]), not [0...N-1].
 * @note The channel number N must be between 1 and 8. If the device is
 * daisy-chained, it will deactivate both the N-th channel of the master board
 * and the N-th channel of the slave board. Remember that in a daisy-chained
 * configuration, both boards share the same configuration.
 */
void ADS1299Manager::configureChannelInput(int N, byte inputCode)
{
    byte reg, config;
        
    // Check the inputs
    if ((N < 1) || (N > NCHAN_PER_BOARD)) return;
    
    // Disable any data collection
    ADS1299::SDATAC(); delay(1);

    // Read the previous configuration
    int N_zeroRef = constrain(N-1,0,NCHAN_PER_BOARD-1);
    reg = CH1SET+(byte)N_zeroRef;
    config = ADS1299::RREG(reg); delay(1);

    // Configure the channel input
    inputCode = inputCode & 0b00000111;         // Bitwise AND to get just the bits we want and set the rest to zero
    config = (config & 0b11111000) | inputCode; // Bitwise AND to clear the input bits and Bitwise OR to set the new input bits

    // Write the new configuration
    ADS1299::WREG(reg,config); delay(1);

	isRunning = false;
};
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

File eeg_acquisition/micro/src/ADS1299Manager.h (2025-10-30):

// The modifications made by Daniel Enériz are licensed under the GNU General Public License v3.0.
//
// Copyright (C) 2024 Daniel Enériz
// 
// This file is part of ADS1299 driver.
// 
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
//  ADS1299Manager.h
//  Part of the Arduino Library for the ADS1299 Shield
//  Created by Chip Audette, Fall 2013
//
//  Modified by Daniel Enériz Orta through March 2024
//  	- Use only ADS1299 functionalities for our project



#ifndef ____ADS1299Manager__
#define ____ADS1299Manager__

#include <ADS1299.h>

#include <Commands.h>

#define NCHAN_PER_BOARD (8)  // number of EEG channels

/*   Arduino Uno - Pin Assignments
  SCK = 13
  MISO [DOUT] = 12
  MOSI [DIN] = 11
  CS = 10; 
  RESET = 9;
  DRDY = 8;
*/

#define PIN_DRDY (8)
#define PIN_RST (9)
#define PIN_CS (10)
#define SCK_MHZ (4)

//gainCode choices
#define ADS_GAIN01 (0b00000000)
#define ADS_GAIN02 (0b00010000)
#define ADS_GAIN04 (0b00100000)
#define ADS_GAIN06 (0b00110000)
#define ADS_GAIN08 (0b01000000)
#define ADS_GAIN12 (0b01010000)
#define ADS_GAIN24 (0b01100000)
#define ADS_GAIN00 (0b01110000) // This does not use the PGA

// dataRateCode choices
#define ADS_DR_16K (0b00000000)
#define ADS_DR_8K (0b00000001)
#define ADS_DR_4K (0b00000010)
#define ADS_DR_2K (0b00000011)
#define ADS_DR_1K (0b00000100)
#define ADS_DR_500 (0b00000101)
#define ADS_DR_250 (0b00000110)

//inputCode choices
#define ADSINPUT_NORMAL (0b00000000)
#define ADSINPUT_SHORTED (0b00000001)
#define ADSINPUT_TESTSIG (0b00000101)
#define ADSINPUT_BIAS_MEAS (0b00000010)

//test signal choices...ADS1299 datasheet page 41
#define ADSTESTSIG_AMP_1X (0b00000000)
#define ADSTESTSIG_AMP_2X (0b00000100)
#define ADSTESTSIG_PULSE_SLOW (0b00000000)
#define ADSTESTSIG_PULSE_FAST (0b00000001)
#define ADSTESTSIG_DCSIG (0b00000011)
#define ADSTESTSIG_NOCHANGE (0b11111111)

// Output modes
#define OUTPUT_TYPE_TEXT (0)
#define OUTPUT_TYPE_BINARY (1)
#define OUTPUT_TYPE_OPENEEG (2)
#define OUTPUT_TYPE_TELEMETRY (3)

#define OFF (0)
#define ON (1)

//binary communication codes for each packet
#define PCKT_START 0xA0
#define PCKT_END 0xC0
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

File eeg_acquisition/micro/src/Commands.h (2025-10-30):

//
//
// Commands.h
//
// This header file contains the definitions of the commands that can be sent to
// the microcontroller connected to the ADS1299 to change its configuration.
// Each command is a defined string

#ifndef _Commands_h
#define _Commands_h

// Channel identifiers
#define CHANNEL_1 1
#define CHANNEL_2 2
#define CHANNEL_3 3
#define CHANNEL_4 4
#define CHANNEL_5 5
#define CHANNEL_6 6
#define CHANNEL_7 7
#define CHANNEL_8 8

// Enable and disable channels: command = "[e|d][channel]"
// Example: "e1" enables channel 1
#define ENABLE_COMMAND 'e'
#define DISABLE_COMMAND 'd'

// Gain settings: command = "g[channel][gain]"
// Example: "g124" sets the gain of channel 1 to 24
#define GAIN_FLAG 'g'

#define GAIN_00 0
#define GAIN_01 1
#define GAIN_02 2
#define GAIN_04 4
#define GAIN_06 6
#define GAIN_08 8
#define GAIN_12 12
#define GAIN_24 24

// Clock output settings: command = "c[0|1]"
// Example: "c1" enables the clock output
#define CLOCK_OUTPUT_FLAG 'c'
#define CLOCK_OUTPUT_ENABLE '1'
#define CLOCK_OUTPUT_DISABLE '0'

// Data rate settings: command = "f[datarate]"
// Example: "f0" sets the data rate to 16kHz
#define DATA_RATE_FLAG 'f'
#define DATA_RATE_16K '0'
#define DATA_RATE_8K '1'
#define DATA_RATE_4K '2'
#define DATA_RATE_2K '3'
#define DATA_RATE_1K '4'
#define DATA_RATE_500 '5'
#define DATA_RATE_250 '6'

// Input settings: command = "i[channel][input]"
// Example: "i1n" sets the input of channel 1 to normal
#define INPUT_FLAG 'i'

#define NORMAL_INPUT 'n'
#define SHORTED_INPUT 's'
#define TEST_SIGNAL_INPUT 't'
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

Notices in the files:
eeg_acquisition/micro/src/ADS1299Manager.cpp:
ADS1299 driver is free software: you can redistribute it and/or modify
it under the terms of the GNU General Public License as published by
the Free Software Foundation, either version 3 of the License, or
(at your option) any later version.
